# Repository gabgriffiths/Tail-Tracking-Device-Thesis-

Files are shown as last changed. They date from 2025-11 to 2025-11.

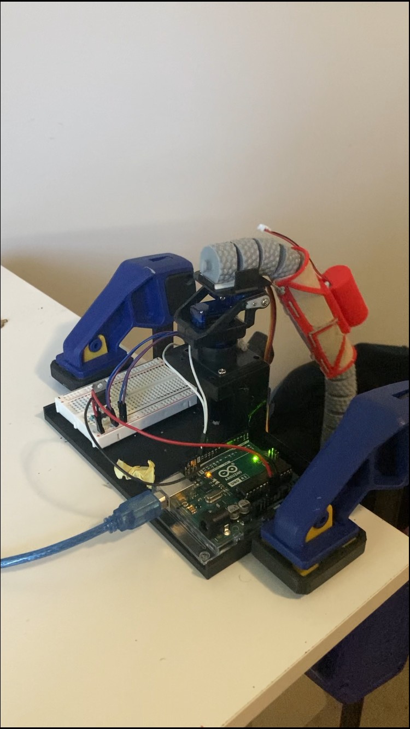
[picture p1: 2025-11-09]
Images/Testing set up.jpg

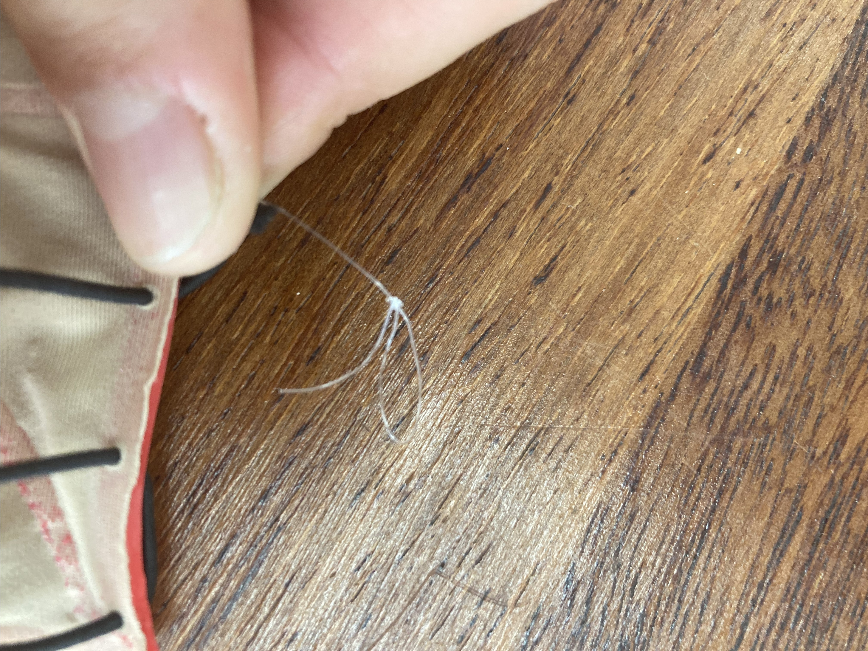
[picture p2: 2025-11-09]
Images/fishing line loops.jpg

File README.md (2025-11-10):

# Tail Tracking Device Thesis
This repository is for the dissemination of results found and desgins created for my honours thesis "Tales for Tails: Development of a Novel Biotelemetry Attachment for Australian Marsupials" (2025).

Abstract of Thesis:

"Biotelemetry tools are developing at a rapid pace with advances like battery miniaturisation and new communication protocols making devices applicable to an increasing variety of environments and species. However, the means of attaching these devices are not improving at the same pace, with collars and glue-on devices still the main techniques of attachments. For Australian marsupials, these methods may result in a rate of injury or death of upwards of 50%, leading to ecological researchers developing their own attachment styles to reduce incidence rates.
This study aims to understand ecological researcher needs for biotelemetry devices, from both human and animal perspectives, and use these requirements to develop a permanent tail-style attachment for safer performance on Australian marsupials. We do so by interviewing 3 ecological researchers on their experiences using biotelemetry devices and develop these into a list of requirements based on animal and researcher needs. These requirements, which largely focus on the wearability of such a device, are then used to guide the iterative design of a tail-style attachment. We tested this attachment on an animated mock tail and found that the device stays on the tail for an extended period and meets most of the requirements originally developed, as evaluated by both the research team and the original researchers interviewed. 
This project develops a successful tail-style attachment for biotelemetry devices yet also suggests that engagement between the ecological and engineering research communities would improve outcomes for both parties and accelerate the rate of technology adoption for environmental monitoring. Strengthening collaboration between these communities will improve our understanding of our world during a period of impending climate and extinction crises."

Included in this repository are:
- Researcher related requirements developed from interviews
- Animal related requirements developed from interviews and research
- Final Design for project
- Instructions for printing and putting together this device
- Photos of the device

# **Instructions for Device Use**

**3D Printing on Fabric**
The process of printing on to fabric involved cutting out a section of fabric the width of the 3D printer base plate. One of the short edges of the fabric was then taped down with masking tape (although any tape would likely work) as close as possible to the edge of the base plate, then the opposing edge was stretched across the base plate and taped down as close as possible to the other edge of the base plate. Occasionally, the original side of fabric would need to be adjusted to ensure as flat a surface as possible. Then, the 2 long edges were individually stretched and taped down. The aim of this process is to get a flat surface across the fabric with very little give anywhere in the fabric. If the fabric is not flat, or there is a loose section, the print head will likely snag in the fabric, ripping the fabric, ruining the print and potentially damaging the printer. 

**Preparing the attachment for deployment:**

The process of assembling this attachment would involve printing the base on to a section of elastane fabric and printing the electronics case directly. Once printed, the elastane fabric needs to be trimmed to the base dimensions, and then the base is loosely laced, such that the attachment still lies flat. Lacing should begin at opposite ends and sides of the attachment, and finish at the fourth hole (middle hole) on each side. The solenoid should be positioned in the centre of the solenoid cut-out in the base print. Care should be taken to position the solenoid accurately, as the solenoid has 2mm tolerance to the edge of the solenoid cut-out, but only 0.5mm tolerance to the case once inserted. If the solenoid is poorly placed, the electronics case will not fit to the base. The ends of the lacing should then be thread along the middle grooves and through the internal cut-outs of the base, with an Angler’s Loop knot or similar tied into the end of the lacing material. These loops should then be carefully slipped over the end of the solenoid pin; using a small instrument like a needle may help. The tracking case and electronics of the device are then inserted and positioned carefully into the electronics case; an adhesive can be used within the device to reduce movement of these instruments. However, the case is designed to cradle the device as the sides of the cylinder extend to 145 degrees, which curve around the device to provide support and reduce the likelihood of the device falling out. An adhesive should be conservatively applied in the L-shaped cut-outs of the base and then the electronics case carefully slid in over the top of the solenoid. More adhesive should then be applied on the outside of this joint to improve weatherability. 

**Deploying the device:**

In the field, once an animal is caught and bagged (a process where the animal’s upper body is placed inside a hessian bag to calm them [3, 20]), the handler can position the tail to lie along their lap. The loosely laced attachment is slipped over the end of the tail and positioned at the rump. The lacing is then tightened such that the device is flush to the tail yet not constricting, and knots tied in the end to secure to the tail, after which the animal may be released.

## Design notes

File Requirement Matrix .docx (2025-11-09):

Researcher-Specific Requirements

Table 17 Researcher specific requirements for animal tracking devices and the expected thresholds a product should meet, as collated from initial requirement gathering interviews and literature reviews. These are grouped into the overarching concerns: cost; attachment; variables collected; interface – design and delivery; interface – data visualisation and analysis; battery.

Overarching Concern | # | Specific Requirement | Poor | Adequate | Excellent
Cost | 1 | Cost of overall system to be reduced (w/o Tag costs) | >$2000 (AUD) | $1000<Cost<$2000 | <$1000
| 2 | Cost per tag reduced | >$1000 (AUD) | $250<Cost<$1000 | <$250
| 3 | Cost of customisability and design reduced | No customisability available | Design included in pricing | Device design allows for DIY customisation (no additional cost)
Attachment | 4 | Available from Manufacturer | No Attachment style available from manufacturer – only tag available | 1 Attachment style available | 1+ attachment style available
| 5 | Attachment Style for Peramelemorphia (and other marsupials) available | No Suitable Attachment Available | | Suitable Attachment Available
| 6 | Attachment is modifiable to suit species specific requirements | Attachment specifications are rigid and unchangeable | Attachment allows for specification changes at manufacture level | Attachment allows for specification changes in-field
| 7 | Attachment reliably detaches within study period | No detachment mechanism | Natural Detachment | Programable detachment
| 8 | Attachment is intuitive with clear instructions | Not intuitive, need expert guidance | Intuitive, though no clear instructions provided by manufacturer OR Unintuitive, but instructions are clearly provided and useable | Intuitive, and manufacturer provides clear instructions for attachment and use
| 9 | Attachment in-field is not laborious | Requires 2 people Takes more than 15 mins post-capture | Requires 1-2 people Takes 10-15 mins post-capture | Requires 1 person Takes less than 10 mins post-capture
| 10 | Attachment is weather resistant | Water and dust can easily permeate the design Fabrics used in the design absorb water | 1 of the 2 requirements listed is met | Water and dust cannot permeate design Fabrics used in the design are non-absorbent
Variables Collected | 11 | Positioning as standard
| 12 | Positioning is accurate | Accuracy >20m | Accuracy 5-20m | Accuracy <5m
| 13 | Accelerometer/Activity Metrics Available | Unavailable | | Available
| 14 | Proximity Metrics Available | Unavailable | | Available
| 15 | Core Temperature Metrics Available | Unavailable | | Available
| 16 | External Temperature Metrics Available | Unavailable | | Available
| 17 | Other Environmental Metrics Available | Unavailable | | Available
Interface – Design and Delivery | 18 | Software interface is intuitive and easy to use | Software interface is unintuitive and clunky. It is difficult to find where information is displayed or stored. Data is stored in databases/lists and is not readily visualised | 2 of the 3 of the listed requirements are met. Ie. Software is intuitive but data isn’t easily visualised. | Software interface is intuitive and flows easily between different information types/data. It is easy to find where information is displayed or stored. There are multiple ways to access information, however, there is one centralised way (through side tabs) to access anything required. Data is stored in databases that can be accessed for download, but are also readily visualised in different means.
| 19 | Software is appropriate for data extraction and analysis | Software does not store location, activity and any other sent data, with timestamps and animal ID in a database OR stores but without explicit animal id or time stamp OR Stores all but download is unavailable | Software stores location, activity and any other sent data, with timestamps and animal ID in a database Download is available as a CSV file. | Software stores location, activity and any other sent data, with timestamps and animal ID in a database The database is available for download at any time. The animal id and time can be filtered with search functionality, and desired variables chosen. Download is available as a CSV file.
| 20 | Interface is appropriate for “real-time” location and activity monitoring | Interface does not allow for easy access to a map for “real time” location-monitoring Interface does not publish “real time” activity (“low”, “med”, “high”) | 1 of the 2 requirements listed are met | Interface allows for easy access to a map for “real time” location-monitoring Interface does not publish “real time” activity (“low”, “med”, “high”)
Interface- Data Visualisation & Alerts | 21 | Animal “real time” location visualisation | Animal “real time” location data is available but not visualised | | Animal “real time” location data is available and visualised
| 22 | Animal activity data visualisation | Animal activity data is available but not visualised | | Animal activity data is available and visualised
| 23 | Environmental data (from base stations or otherwise) | Environmental data is available but not visualised | Environmental data is available, and visualised as pinpoint data | Environmental data is available, and visualised as a gradient over the landscape
| 24 | Animal Reduced Activity alerts (for animal endangerment OR dropped tracker) | No alert available for changes in animal activity level | Animal activity alert triggers based on if activity level is low OR Animal activity alert triggers based on if location data is stagnant for >12 hrs | Animal activity alert triggers based on if activity level is low AND Animal activity alert triggers based on if location data is stagnant for >12 hrs
| 25 | Environmentally Dangerous Conditions Alert | No alert available for dangerous environmental conditions | Dangerous environment alert triggered by extreme heat | Dangerous environment alerts are differentiated and triggered by high heat AND high heat/high winds (potential fire alert)
Battery | 26 | Appropriate # of fixes per day | Number of fixes per day are unreliable. Not at least 1 fix per day | Number of fixes per day is consistent At least 1 fix is made per day | Number of fixes per day is consistent More than 1 fix is available per day (0.5) At least 4 fixes are available per day (1)
| 27 | Battery life is >1 year at appropriate (2) fix rate | Battery life is <2 months. | Battery life is 2-6 months. | Battery life is >6 months
| 28 | Attachment style is not battery intensive and does not significantly reduce battery life | Attachment uses more than 100J | Attachment uses between 1-100J | Attachment uses less than 1J

Animal-Specific Requirements

Table 18 Animal specific requirements for animal tracking devices and the expected thresholds a product should meet, as collated from initial requirement gathering interviews and literature reviews. These are grouped into the overarching concerns: attachment; weight; behaviour.

Overarching Theme | # | Specific Requirement | Poor | Adequate | Excellent
Attachment | 1 | Attachment Style is suited to Peramelidae, and is not affected by jaw/neck/head shape, nor by behaviour | Attachment falls off or causes injury and/or death | Attachment is loose fitting or causes injury | Attachment is well-fitted, is unaffected by marsupial behaviours, and does not cause injury and/or death
| 2 | Attachment in-field is non-invasive and non-stressful to animal | Requires 2 people Takes more than 15 mins post-capture Is laborious and intrusive to animal (a lot of manipulation required, tight-fitting and/or difficult to attach) | Requires 1-2 people Takes 10-15 mins post-capture Is difficult but manageable to attach, and non-intrusive | Requires 1 person Takes less than 10 mins post-capture Is simple and manageable to attach, without requiring any manipulation of the animal
| 3 | Attachment is elasticated for weight fluctuations | Non-elasticated | | Elasticated
| 4 | Attachment style is delicate on skin, and does not cause rubbing resulting in skin injuries | Attachment is either too tight-fitting that blood flow is impeded, or too loose to cause movement of attachment. Material used is rough, not dermatologically tested, and is affected by moisture/heat fluctuations. Material/design is non-breathable, and traps moisture. | 2 out of 3 of the listed requirements are met. | Attachment is elasticated to adjust with weight fluctuations, where the level of elastication allows for a snug but not tight fit. Material used is soft, dermatologically tested/used in human health settings, and is unaffected by moisture/heat fluctuations. Material/design is breathable and does not trap moisture.
| 5 | Attachment lasts for an extended period, to reduce intrusion to animal | Attachment last for <2 months. | Attachment last for 2-6 months. | Attachment last for >6 months
| 6 | Attachment is suited to attachment of mature juveniles | Attachment does not fluctuate with weight Attachment size is non-suited to juvenile ie. length | 1 of the 2 requirements listed is met | Attachment fluctuates with weight and is a suitable size for the animal both as a juvenile and as an adult ie. for a tail attachment length of attachment is not too long for a juvenile
| 7 | Attachment should not impact survivability or breeding-success.
Weight | 8 | Total System weight is appropriate for small marsupials*, especially Peramelidae | Weight is >25g | Weight is 15g to 25g | Weight is <15g
Behaviour | 9 | Tracker does not cause changes in behaviour | Tracker is intrusive to some degree and the animal continually attempts to remove | Tracker is intrusive to some degree, yet the animal adjusts to within 15 mins. Animal does not try to remove past this stage. | Tracker is non-intrusive when attached and the animal does not attempt to remove
| 10 | Tracker is not removable by animal | Tracker is easily removed by animal (within 24 hrs) | | Tracker cannot be easily removed by animal (within 24 hrs)
| 11 | Tracker easily detaches when programmed detachment occurs | Tracker is not detached from animal within 1hr | Tracker reliably detaches from animal within 15mins-1hr | Tracker reliably detaches from animal within 15mins

*Includes the following Families: Peramelidae, Perorycitidae, Myrmcobiidae, Dasyuridae, Potoridae, Thylacomidae, Macropodidae.
These families include species with body mass ranging from 500-9000g.

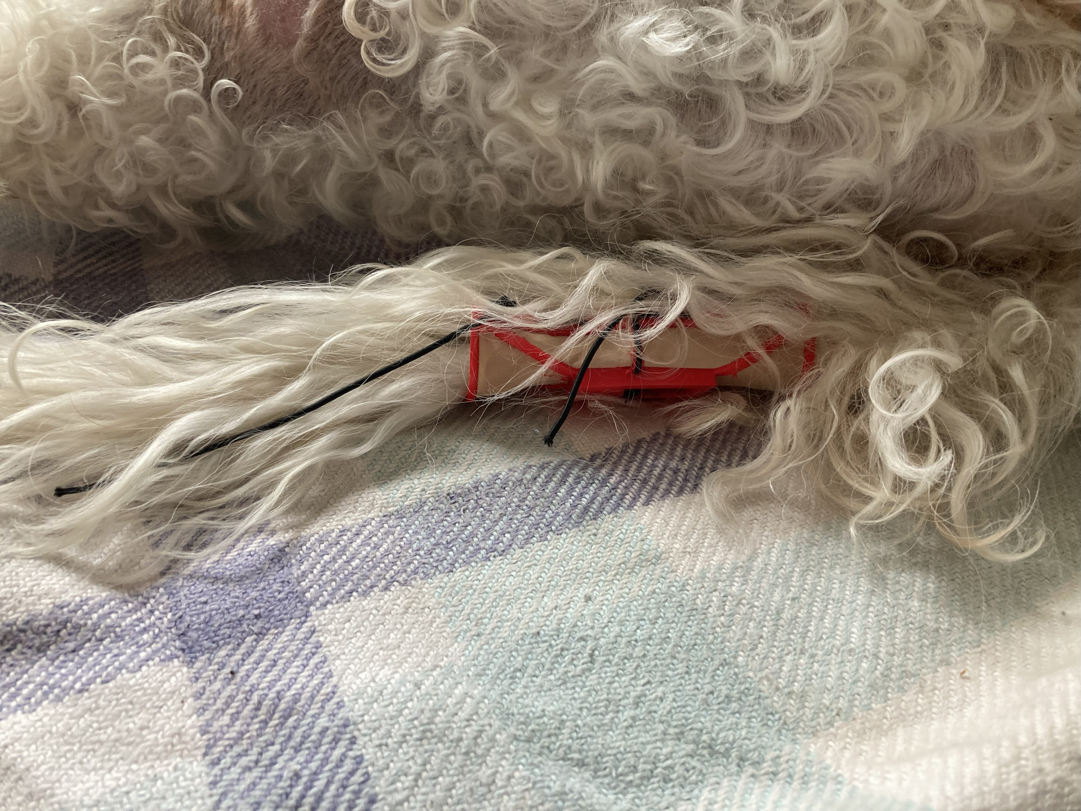
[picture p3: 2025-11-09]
Images/On_dog.jpg

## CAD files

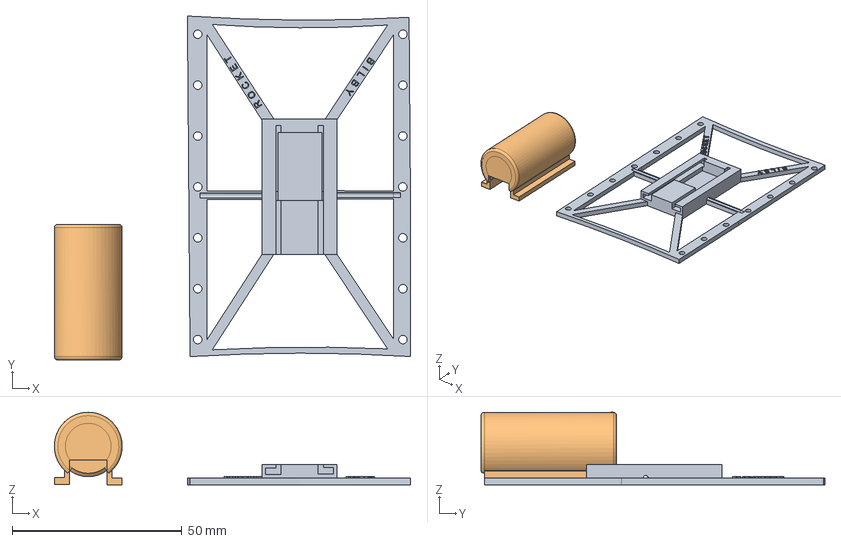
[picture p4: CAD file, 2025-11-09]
Device_Designs/Removeable+Cap.stp
105.0 x 101.4 x 21.4 mm
Base
Removable Lid

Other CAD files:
Device_Designs/Removeable+Cap.dwg
Device_Designs/Removeable+Cap.f3d

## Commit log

2025-11-10 Rename IMG_2448.HEIC to Final Prototype on Tail.HEIC
2025-11-10 Rename Pre-processing.heic to Final Prototype as printed.heic
